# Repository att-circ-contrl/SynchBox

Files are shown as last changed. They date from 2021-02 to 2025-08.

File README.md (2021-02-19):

# "I/O SynchBox" Data Logger and Timing Signal Generator

## Overview

The I/O SynchBox is a USB-connected device designed to synchronize and
collect data from several pieces of equipment:

* It can generate two independent timing signals (TTL pulse trains on BNC).
* It can assert individual TTL pulses on two independent BNC outputs
(typically used for control of external equipment).
* It can emit 16-bit data words on a rectangular (ribbon cable) connector.
This is typically used to send "event codes" to e-phys recording equipment
and/or to eye-tracker equipment.
* It can read analog inputs on three BNC ports ("X", "Y", and "Z"; typically
analog joystick connections).
* It can read from light sensors on two BNC ports ("L" and "R"; typically
connected to an experiment computer monitor for frame synchronization).

The SynchBox has an internal real-time-clock with 0.1 ms precision. Event
reports (with timestamps) are sent to the host computer over a USB serial
link. Analog inputs are polled at a user-configured rate, and reported
(with timestamps) at the polling interval.

Clock drift is nominally 100 parts per million or better (the precision of
the clock crystal on the "Arduino Mega 2560" microcontroller board).

The I/O SynchBox project is copyright (c) 2021 by Vanderbilt University,
and is released under the Creative Commons Attribution-ShareAlike 4.0
International License.

## Quick-Start

The top-level Makefile automates common operations (under Ubuntu-derived
Linux, at least):

* Type "`make`" without arguments for the Makefile target list.

* To rebuild the manuals (which should already be in the "`manuals`" folder),
type "`make manual`".

* To flash an I/O SynchBox using the firmware hex file, plug the device
into your computer and type "`make burn`".

* To rebuild the firmware for the I/O SynchBox, make sure the "NeurAVR"
project is installed and "`neuravr`" is symlinked at an appropriate
location (in the "`code-firmware`" folder or in the folder the "`SynchBox`"
project is installed in), and type "`make hex`".

* To build release packages for all of the I/O SynchBox's hardware
components and peripherals, type "`make hwpkgs`". Board fabrication
files, meshes, and various documentation files are left in subfolders in
the "`packages`" directory.

## Remarks

This project is at a milestone state, and is in service, but future changes
are planned (eventually) that will substantially affect the project's
structure.

The present version will probably be kept as a branch, but the active version
will make major changes:

* For the time being, the firmware includes a shim that allows compiling
with the Arduino IDE instead of the NeurAVR libraries. This is not
guaranteed to be supported in the future (and might already be broken; I
haven't tested it recently).

* While the firmware does use the NeurAVR libraries, it does not presently
use the NeurAVR application skeleton. Version 2 will use that, along with
the ADC libraries and other code presently duplicated in the firmware
source. The end result will be cleaner and more compact but won't build with
the Arduino IDE (the application skeleton source would have to be transcluded
at compile-time, which may eventually be supported but not soon).

* Certain firmware features may be dropped or modified. In particular, event
code strobe  bits aren't actually used by any of our applications, and
timing pulse, reward pulse, and event code generation may be replaced with
more general GPIO signal/pattern generation code. The legacy command set will
probably be kept, for use-case compatibility, but the implementation will
change (and may be moved to a "GPIO device" application library).

* TTL input for timing synchronization really should be implemented (on BNC
lines and on the parallel header). The underlying GPIO implementation will
certainly support that when implemented.

* Right now, all of the printed circuit boards are project-specific. The
boards are very similar to those used for other ACC Lab projects, and will
eventually be merged into a single set of standard boards with as few
project-specific boards as possible. When that happens, all PCB layouts
and front-panel mechanical plans that are not SynchBox-specific will be
moved to that project.

## Folders

* `code-firmware` -- Firmware source code for the SynchBox.
* `datasheets` -- Vendor-supplied datasheets. Under vendor copyright.
* `hardware-main` -- Boards, CAM files, and drawings for the I/O SynchBox
internal components.
* `hardware-periphs` -- Boards, CAM files, meshes, and drawings for external
peripherals and accessories.
* `hexfiles` -- Firmware binaries for the SynchBox.
* `manuals` -- SynchBox documentation.
* `manuals-src` -- Source for rebuilding the SynchBox documentation.
* `notes` -- Assorted notes regarding SynchBox use and development.
* `packages` -- Automatically generated archives packaging relevant files
for making hardware components and peripherals. This typically includes a
`.zip` archive of the gerber files using the naming conventions of the
"Seeed Studio" PCB fabrication service, a `.png` rendering of the board
generated from the gerber files, a `.zip` archive containing g-code
toolpaths for various hardware parts, `.stl` files containing meshes for
various hardware parts, and other documentation as appropriate.
* `photos` -- Selected photographs of the SynchBox and its accessories.
* `utils` -- Various helper scripts.
* `vendor-docs` -- Vendor-provided documentation (other than datasheets).
Under vendor copyright.

Within each hardware component's folder the following subdirectories may be
present:

* `boards` -- Printed circuit board design files. Anything with the `.pcb`
extension was made with the "`pcb`" program (now part of `gEDA`).
* `boards/gerber` -- Files for printed circuit board fabrication as generated
by `pcb`.
* `boards/plots` -- Manually assembled renderings of the circuit board layout.
* `cad` -- CAD files (mechanical models) for cases and faceplates. Files with
the `.fcstd` extension were made with the "`FreeCAD`" program. Files with
`.iges` and `.step` extensions are models exported to industry-standard
formats that can be imported into different CAD programs.
* `diagrams` -- Illustrations that are not mechanical drawings.
* `drawings` -- Mechanical drawings of boards, cases, and faceplates.
* `mech` -- CAM files (toolpaths) for cases and faceplates. Files with the
`.crv` extension were made with Vectric's `VCut` program. Files with the
`.crv3d` extension were made with Vectric's `Aspire` program but can probably
be imported into `VCut`. Files with the `.txt` extension are g-code; the tool
for each g-code file is usually indicated in the filename.
* `meshes` -- STL meshes for 3d printed parts.
* `notes` -- Assorted design documentation not covered above.
* `packages` -- A symbolic link to the project's sub-folder in the
top-level "`packages`" directory.
* `renders` -- Renders of mechanical models of cases, faceplates, and
assemblies.
* `schematics` -- Manually generated schematics for printed circuit boards.
Anything with the `.fig` extension was made with the "`xfig`" program.

Regarding the software tools used:

* I have a love/hate relationship with the `pcb` program. It works _just_
well enough that it isn't worth my time to learn a new program, but the
parts of the interface that I use have gone steadily downhill since 2003.
It also won't check a layout against a netlist, which is vital for anything
more complicated than the boards in this project. If you need to modify
existing board layouts, I suggest importing the gerber files into your
preferred PCB CAD program rather than trying to use the design files as-is.

* I have a love/hate relationship with the `FreeCAD` program. It works
_just_ well enough that it isn't worth my time to learn a new program, but
it has very strange ideas about how many operations should be done and it
lacks several features that would be very helpful for building models. If
you need to modify existing mechanical models, I suggest importing `.step`
or `.iges` models into your preferred CAD program.

* I've had good experiences with Vectric's CAM software, and the price for
`VCut` is reasonable for hobbyists. This generates 2D toolpaths at multiple
depths, so it's fine for cases and faceplates for electronics. That said,
it should be possible to convert EPS to DXF and import DXF into any CAM
program, or to reimplement the case designs very quickly using the mechanical
drawings, so any CAM program should be sufficient if you need to generate
new toolpaths.

_This is the end of the file._

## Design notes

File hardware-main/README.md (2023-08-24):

# "I/O SynchBox" Hardware -- Main Unit

## Overview

The "I/O SynchBox" consists of a "shield" that sits on top of an "Arduino
Mega 2560" board, with ribbon-cable headers connecting the shield to
various faceplate boards. This decouples the shield design, faceplate board
design, and choice of enclosure (each may be varied without needing to
redesign the other, as long as headers are kept consistent).

**NOTE** -- Some or all of these boards will eventually be replaced with
general-purpose variants in their own project.

## Folders

* `mech-aux` --
Folder for mechanical models used by several components.
* `notes` --
Folder for auxiliary information for building the SynchBox.
* `v2-backpanel` --
Faceplate board with 8 TTL BNC connectors and a USB 2.0 B
power-and-communication port.
Fits in Hammond's aluminum box end-panels, should fit a 1u rack panel.
* `v2-frontpanel` --
Faceplate board with 5 analog input BNC ports, reset switch, status light,
and a rectangular connector with 16-bit digital output.
Fits in Hammond's aluminum box end-panels, should fit a 1u rack panel.
* `v2-shield` --
"Shield" board for use with an "Arduino Mega 2560" board. Maps analog
header pairs 4 and 5 to light sensor circuitry (pull-ups and pre-amplifier
circuits).

_This is the end of the file._

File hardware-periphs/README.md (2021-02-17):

# "I/O SynchBox" Hardware -- Peripheral Devices

## Overview

Various peripherals have been built for the "I/O SynchBox". Most of these
are used to map TTL outputs from the rectangular connector on the SyncBox
front panel to TTL inputs on other pieces of equipment. This allows "event
codes" to be sent from the SynchBox that are used to align data recorded by
the SynchBox's host computer with data recorded by these other devices.

Other peripherals exist and are noted below.

## Folders

* `adapter-brainamp` --
Adapter for a 3-row 26-pin D-sub connector used by the Brain Products
"BrainAmp" device.
* `adapter-intan` --
Adapter mapping 8-bit 10-position cables (from the "`ribbon-splitter`"
adapter) to pins that mate with the digital I/O terminal blocks on the
Intan "I/O Expander" used with Intan's "RHD" and "RHS" series recording and
stimulation controllers (respectively).
* `adapter-neuroscan` --
Adapter for a 25-pin D-sub connector used by the Compumedics "NeuroScan"
device.
* `adapter-tobii` --
Combination splitter/adapter mapping the least-significant 8 bits of the
SynchBox's TTL output to a 9-pin D-sub connector used by the Tobii "Pro
Spectrum" eye-tracker. All TTL ouputs are also passed through to a second
ribbon cable connector.
* `chuck-standalone` --
Hardware and firmware for a stand-alone device that communicates with a host
computer in a similar manner to the SynchBox, relaying data from a Nintendo
"Wii Nunchuck" joystick.
* `joystick-2016` --
Scematics for a ruggedized analog joystick used in 2016 epxierments.
* `light-sensor-clamp` --
3d printed clamp used for mounting light sensors on the corners of monitors.
Patches of the screen under the light sensor are strobed to encode data, and
the SynchBox reads the resulting analog signals to allow timing
reconstruction with sub-frame accuracy.
* `ribbon-splitter` --
Splitter converting the 16-bit 34-position rectangular connector TTL output
to two 8-bit 10-position rectangular connector outputs.

_This is the end of the file._

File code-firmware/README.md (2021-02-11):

# Attention Circuits Control Laboratory - I/O SynchBox project
# README documentation.
Written by Christopher Thomas.

## Important things to note:

* Arduino's development environment will auto-detect and include any file
that has a `.ino`, `.c`, `.cpp`, or `.h` extension.

* The Arduino IDE doesn't like hyphens in filenames; use underscores instead.

* I gave the Makefile a customized name to avoid confusing the Arduino IDE.
It will generate its own Makefile when building the project.

* **Building with the Arduino IDE is possible but not officially supported.**
There are shims in place for it, and it may be officially supported again
in the future, but for now it's not guaranteed to work.

## Building using the NeurAVR library and "`make`":

To build using the NeurAVR library, use:

`make -f Makefile.neuravr NEURAVRPATH=(path) (targets)`

Type `make` for a list of available targets. Typical targets are:

* `clean` -- Removes binaries so that the Arduino IDE doesn't complain
about them.
* `hex` -- Builds the hex files (and copies them to the top-level hex
folder).
* `burn` -- Calls `avrdude` to write the hex image to `/dev/ttyACM0`.
* `test` -- Connects to `/dev/ttyACM0` using the `cu` serial client.

The `NEURAVRPATH` variable defaults to looking for `neuravr` in the build
directory. This is a symlink to the `NeurAVR` project tree; the symlink
can be changed as an alternative to specifying a path variable.

## Building using the Arduino IDE:

* Copy (or symlink) the project directory into your Arduino sketchbook
  directory. The directory name must match the name of the top-level .ino file
  (so, "synchbox" for this project).

* Open and edit the project per normal.

* On my machine, under Linux, the Arduino IDE sometimes can't open the serial
port to burn the sketch. Once you've found the hex file, the sketch can be
burned manually using:

`avrdude -c stk500 -p m2560 -P (port) -D -U flash:w:(file):i`

...Where "`(port)`" is usually `/dev/ttyACM0` or `/dev/ttyUSB0` under Linux,
and `(file)` is the hex file.

The Arduino IDE puts the hex file in:

`/tmp/build(gibberish).tmp/(filename).hex`

Use "`ls -t /tmp|grep build|head -1`" to find the right build directory;
every build attempt will create a new directory, so there will be several
of them.

_This is the end of the file._

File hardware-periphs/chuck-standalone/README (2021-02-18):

This code is intended to interface with the "Adafruit Pro Trinket 5V", which
is a smaller-form-factor variant of the Arudino Pro/Arduino Pro Mini, using
an ATmega328P chip at 16 MHz (as with the Arduino Uno).

An Adafruit "Nunchucky" board was used as the Wii Nunchuck break-out adapter.
If memory serves, it mated directly with the digital I/O pins on the
Pro Trinket, but it's been many years so I no longer remember the details.

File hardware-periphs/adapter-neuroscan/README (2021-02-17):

This board didn't work!

I had to remove the isolator chips and bridge across their pads to make a
pass-through, instead of using isolation.

This passed multiple desk-checks against the chips' datasheets, so I'm not
sure what went wrong.

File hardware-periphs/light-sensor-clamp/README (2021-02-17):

See the LICENSE file for distribution information.

Each clamp consists of three 3D printed parts, and two McMaster-Carr parts.

The 3D printed parts are the body of the clamp (yellow in the assembly
diagram), the wire-holding cap (green in the assembly diagram), and the
sensor locator cap (red in the assembly diagram).

To assemble the clamp:

- Affix the foot (p/n 6111K451) to its feed hole in the clamp body, either
by gluing the foot's mounting nut to the body or by gluing a 1/4"-20 threaded
insert into the feed hole in the clamp body.
- Verify that the foot travels freely, and glue the knob (p/n 6214K26) to
the foot's threaded rod.
- Feed the TEPT4400 phototransistor's leads through the locator cap's holes.
- Feed the BNC pigtail's leads through the body of the clamp out of the
sensor hole.
- Solder the phototransistor's leads to the BNC pigtail's leads, using
heat shrink or tape to avoid short circuits.
- Press-fit the locator cap into the clamp body.
- Slide the wire cap on to the BNC pigtail's leads.
- Press-fit the wire cap on to the clamp body.

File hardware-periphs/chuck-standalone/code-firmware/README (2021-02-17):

Important things to note:

- Arduino's development environment will auto-detect and include any file
  that has a .ino, .c, .cpp, or .h extension.

- The Arduino IDE doesn't like hyphens in filenames; use underscores instead.

- I gave the Makefile a customized name to avoid confusing the Arduino IDE.

Using the NeurAVR library and not the Arduino IDE:

- FIXME - The NeurAVR does not yet support I2C, so building this way will
give you bogus data!

- To build using the NeurAVR library instead of using Arduino, use
"make -f Makefile.neuravr (optional target)". Default target is "hex";
"clean" removes binaries so that the Arduino IDE doesn't complain about them.

- Development targets are "burn" (using the bootloader), "isp" (using the
AVRispMk2 programmer), and "test" (trying to contact using "cu"). These only
work on my personal machines; you'll have to edit them to get them working
on your systems (these are convenience-targets; these tasks can be done
manually easily enough).

Using the Arduino IDE:

- On my machine, under Linux, the Arduino IDE sometimes can't open the serial
  port to burn the sketch. The sketch can be burned manually via:

  avrdude -c stk500 -p m2560 -P /dev/ttyACM(number) -U flash:w:(hex file):i

  (The -D flag may also be needed if flash-erase fails.)

  The Arduino IDE puts the hex file in
  /tmp/build(gibberish).tmp/(filename).hex.
  Use "ls -t /tmp|grep build|head -1" to find the right build directory.

- There may also be shenanigans connecting to the serial port. To do this
  manually, use:

  cu -l /dev/ttyACM(number) -s (baud)

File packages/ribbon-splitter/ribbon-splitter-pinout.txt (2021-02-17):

On the original 34-pin header, even pins are ground, pins 1..31 are digital
outputs (LS pin 1), and pin 33 is +5V.

On the 10-pin output headers, pin 1 is ground, pins 2..9 are digital outputs
(LS pin 2), and pin 10 is ground.

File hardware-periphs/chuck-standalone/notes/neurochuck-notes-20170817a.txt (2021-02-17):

From thomasc@cse.yorku.ca Thu Aug 17 10:47:26 2017
Date: Thu, 17 Aug 2017 10:47:26 -0400 (EDT)
From: Christopher Thomas <thomasc@cse.yorku.ca>
To: Ben Voloh <ben.voloh@gmail.com>, Marcus Watson <marcusrwatson@gmail.com>
Subject: Neurochuck firmware

   In case anyone besides me wants to flash more of these, here's the 
firmware image for the version of the "neurochuck" I have now. This should 
work on any 16 MHz ATmega328P system, including the Uno and Pro Trinket.

   (The 3.3V Pro Trinket runs at 12 MHz instead, which will throw off 
timing, including baud rate timing.)

   It supplies "power" and "ground" to Ain3 (C3) and Ain2 (C2), 
respectively. It uses the LED on Dio13 (B5/SCK) for status indication. If 
you pull down Dio8 (B0) during boot, it'll start spitting out packed data 
automatically without you having to tell it to (this is how it would work 
if I put it in the Neurarduino box).

   The command interface is very similar to the Neurarduino's. Connect at 
115200 baud, type "hlp" or "?" for help, and "idq" to query the device 
type string (so that you can tell this and the neurarduino apart).

   With timestamps enabled (default for manual mode), output looks like:

   TnnnnnnnnJxxyycLxxyyzz

   Without timestamps (default for autostart mode), output looks like:

   JxxyycLxxyyzz

   Joystick (J) and accelerometer (L) values are 8-bit hex-encoded bytes. 
Button values are one hex digit (0-3 in practice; C is bit 0 and Z is 
bit 1).

   If you want a packaged version immediately, I have a case on-hand that I 
can put it into if you don't mind rough-cut holes. Otherwise let me know 
how you want me to proceed with it.

Regards,
 				-Christopher Thomas

    [ Part 2, ""  Text/PLAIN (Name: "neurochuck-20170817.hex") ~30 KB. ]
    [ Unable to print this part. ]

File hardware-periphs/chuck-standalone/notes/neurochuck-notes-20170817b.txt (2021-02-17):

From thomasc@cse.yorku.ca Thu Aug 17 15:06:30 2017
Date: Thu, 17 Aug 2017 15:06:29 -0400 (EDT)
From: Christopher Thomas <thomasc@cse.yorku.ca>
To: Ben Voloh <ben.voloh@gmail.com>
Cc: Marcus Watson <marcusrwatson@gmail.com>
Subject: Re: new nunchuk idea

   I've attached the code, and an updated hex file (I'd forgotten that 
buttons were negative-logic in the raw data; this has been fixed).

   I gave the templates for output in a previous email. Actual test-run 
output is as follows:

(no timestamps; LTS 0):

J7b801L8461b0
J7c811L7f5db2
J7b800L8160b2
J7c810L7f60b0
J7b801L7f5ab4
J7b800L805fb2
J7b800L815db0
J7c802L825eb2
J7b802L805bb1
J7b802L815db3
J7b802L805db1
J7c812L835db6
J7b802L815cb9
J7b800L8c5cad
J7b800L9b5398
J7b800L944d93
J7b800L8c4d99

(with timestamps; LTS 1, the default):

T0002d453J7cff0L8c69af
T0002d83bJ7cff0L8d57b1
T0002dc23J7bff0L8c56a9
T0002e00bJ7cff0L8d57ab
T0002e3f3J7cff0L8d57ac
T0002e7dbJ7cff0L8d58ad
T0002ebc3J7bff0L8d58ad
T0002efabJ7cff0L8f56a8
T0002f393J7b800L984d9a
T0002f77bJ7b800La04d91
T0002fb63J7b800L866196
T0002ff4bJ7b800L628493
T00030333J7c800L1995a5
T0003071bJ7b800L37848c
T00030b03J7b800L3b8988
T00030eebJ7b800L468c91
T000312d3J7b800L468595

(the status screen; QRY):

System state (all values in base 10):
   Version:  20170810
   Timestamp:  54900 ticks
   Clock ticks per second:  10000
   Nunchuck detected:  YES
   Nunchuck polling interval:  100 ticks
   Nunchuck data scrambling:  OFF
   Automatic start:  NO
   Logging:  OFF
   Log interval:  1000 ticks
   Log timestamps:  ON
   Blink codes:  ON
   Clock ticks per blink code bit:  625
End of system state.

(the identity string; IDQ):

devicetype: Neurochuck  subtype: v1  revision: 20170810

(the help screen; HLP or ?):

Commands:
  ?, HLP  :  Help screen.
     QRY  :  Query system state.
   ECH 1/0:  Start/stop echoing typed characters back to the host.
     IDQ  :  Device identification string query.
     INI  :  Reinitialize (clock reset and events idled).
   LOG 1/0:  Start/stop reporting log data.
     LIN n:  Set the data reporting interval to n ticks.
   LTS 1/0:  Include/don't include timestamps in log reports.
     KIN n:  Set the nunchuck polling interval to n ticks.
   BLN 1/0:  Enable/disable status LED blinking.

Regards,
 				-Christopher Thomas

    [ Part 2, ""  Application/X-TAR (Name: "neurochuck-20170817.tar") 84 ]
    [ KB. ]
    [ Unable to print this part. ]

    [ Part 3, ""  Text/PLAIN (Name: "neurochuck-20170817-5v.hex") ~30 KB. ]
    [ Unable to print this part. ]

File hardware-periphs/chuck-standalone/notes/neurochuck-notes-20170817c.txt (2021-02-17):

From thomasc@cse.yorku.ca Thu Aug 17 15:11:46 2017
Date: Thu, 17 Aug 2017 15:11:46 -0400 (EDT)
From: Christopher Thomas <thomasc@cse.yorku.ca>
To: Ben Voloh <ben.voloh@gmail.com>
Cc: Marcus Watson <marcusrwatson@gmail.com>
Subject: Re: new nunchuk idea

   As with the Neurarduino code, you can dump it all into a sketchbook 
directory and build it using the IDE as-is, or you can use "make -f 
Makefile.neuravr" to build against the "neuravr" libraries that I'd made 
for the Neurarduino and related hardware.

   The custom libraries don't have I2C yet, so I recommend using the 
Arduino IDE if you want it to actually sense nunchuck data.

   To talk to the dongle, connect via USB serial port at 115200 baud.

   The status LED is blinking on and off when it can't find the nunchuck, 
is solid-on with an off-blip every 2 seconds when it found the nunchuck 
but you haven't requested data, and is off with a pair of on-blips every 2 
seconds when it's streaming data to you.

   Pulling digital pin 8 to ground triggers "automatic" mode, where it 
starts streaming on startup rather than waiting for you to ask it to. In 
that mode, it omits timestamps and sends data as fast as possible 
(equivalent to LIN 0, KIN 0, LTS 0, LOG 1).

   I'll bring the dongle (and Marcus's Neurarduino) back to Marcus's desk 
as soon as I've finished taking measurements for the case.

Regards,
 				-Christopher Thomas

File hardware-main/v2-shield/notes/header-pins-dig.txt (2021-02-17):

Pin mappings for "digital I/O" header (10-pin, back panel BNC):

Header		Function		Arduino		Atmel

D0		debug input		D6		H3
D1		debug output		D7		H4
D2					D8		H5
D3					D9		H6
D4		reward B		D10		B4
D5		reward			D11		B5
D6		sync			D12		B6
D7		sync B			D13		B7

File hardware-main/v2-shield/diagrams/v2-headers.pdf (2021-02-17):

Vdd

Gnd

## Digital I/O

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
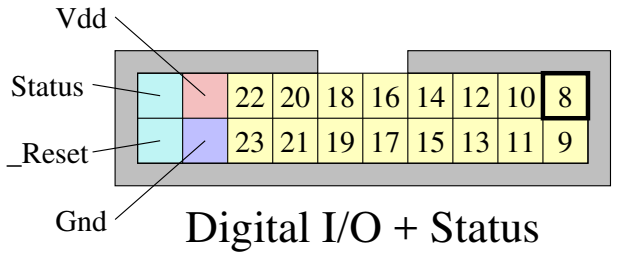
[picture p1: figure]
Digital I/O + Status; Gnd; Status; _Reset; Vdd
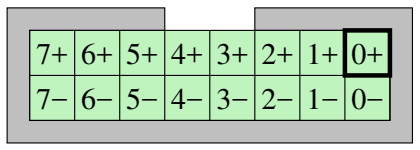
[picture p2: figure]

## Analog Input

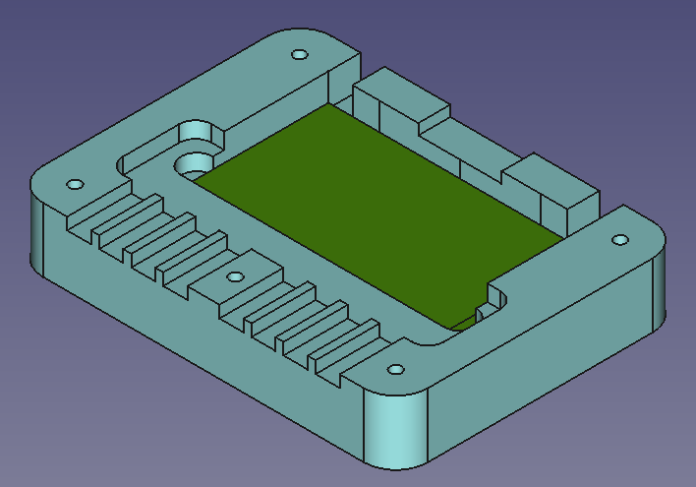
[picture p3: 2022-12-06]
hardware-periphs/ribbon-squid/renders/evcode-squid-shell-bottom.png

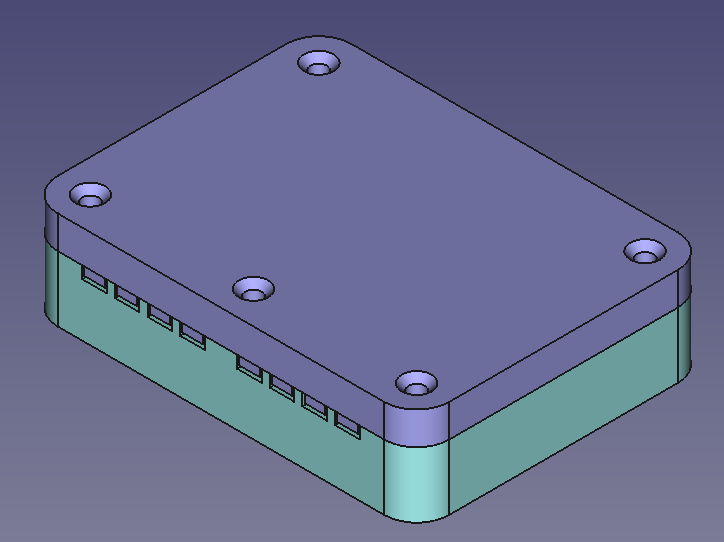
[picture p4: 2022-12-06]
hardware-periphs/ribbon-squid/renders/evcode-squid-shell-closed.png

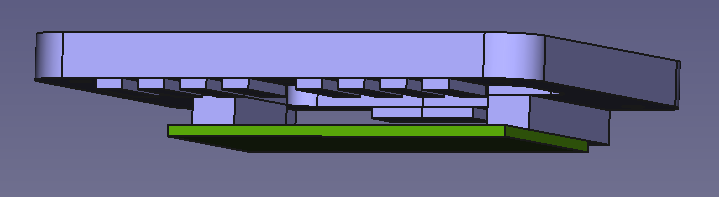
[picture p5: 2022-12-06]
hardware-periphs/ribbon-squid/renders/evcode-squid-shell-top.png

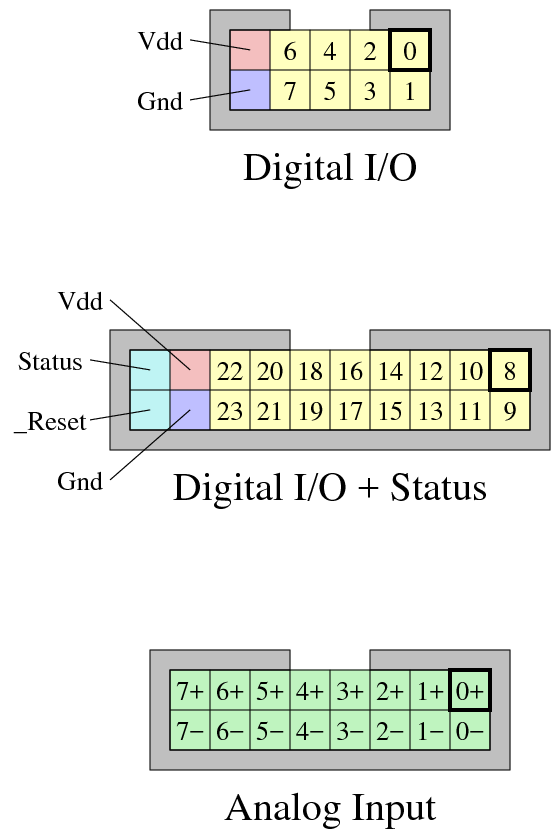
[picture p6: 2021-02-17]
hardware-main/v2-shield/diagrams/v2-headers.png

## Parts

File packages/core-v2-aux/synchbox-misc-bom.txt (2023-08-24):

Bill of materials for additional components for assembling the v2 SynchBox:

Item                             Digikey p/n          Qty

Arduino Mega 2560                1050-1018-ND           1

box metal/abs 8.7"x6.5"          HM906-ND               1

standoff nylon 4-40 F-F 3/4"     36-1902D-ND            4
screw nylon 4-40 3/4"            H550-ND                4
screw nylon 4-40 1/4"            H542-ND                4
hex nut nylon 4-40               36-9605-ND             4

USB A-B cable 6'                 1175-1089-ND           1

This is the end of the file.

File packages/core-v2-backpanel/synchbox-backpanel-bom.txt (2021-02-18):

Bill of materials for the v2 SynchBox back panel:

Item                    Digikey p/n          Qty

header male 2x5 shr     S9169-ND               1

BNC jack (pcb) 50 ohm   WM5278-ND              8

ribbon cable 10pos 6"   H3DDS-1006G-ND         1
USB B panel mount       1528-1570-ND           1

spacer nylon #4 1/16"   492-1071-ND            4
screw metal 4-40 3/8"   HM1456-ND              4
hex nut nylon 4-40      36-9605-ND             4

This is the end of the file.

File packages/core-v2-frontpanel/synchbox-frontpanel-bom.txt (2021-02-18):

Bill of materials for the v2 SynchBox front panel:

Item                    Digikey p/n          Qty

header male 2x8 shr     S9171-ND               1
header male 2x10 shr    S9172-ND               1
header male 2x17 shr    OR984-ND               1

BNC jack (pcb) 50 ohm   WM5278-ND              5
LED green 3mm           4303F5-ND              1
switch pb SPST          SW1021CT-ND            1

ribbon cable 16pos 6"   H3DDS-1606G-ND         1
ribbon cable 20pos 6"   H3DDS-2006G-ND         1

spacer nylon #4 1/16"   492-1071-ND            4
screw metal 4-40 3/8"   HM1456-ND              4
hex nut nylon 4-40      36-9605-ND             4

This is the end of the file.

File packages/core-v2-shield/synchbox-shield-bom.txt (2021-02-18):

Bill of materials for the v2 SynchBox shield:

Item                    Digikey p/n          Qty

header male 1x8         732-5321-ND            5
header male 1x10        732-2670-ND            1
header male 2x18        732-5309-ND            1
header female 2x3       S7071-ND               1
header male 2x5 shr     S9169-ND               1
header male 2x8 shr     S9171-ND               1
header male 2x10 shr    S9172-ND               1

resistor 0805 4.7 ohm   311-4.70CRCT-ND        1
resistor 0805 680 ohm   311-680CRCT-ND         1
resistor 0805 1 kohm    311-1.00KCRCT-ND       2
resistor 0805 2.2 kohm  311-2.20KCRCT-ND       2
resistor 0805 5.49 kohm 311-5.49KCRCT-ND       2
resistor 0805 6.8 kohm  311-6.80KCRCT-ND       2
resistor 0805 10 kohm   311-10.0KCRCT-ND       4
resistor 0805 47 kohm   311-47.0KCRCT-ND       3
resistor 0805 470 kohm  311-470KCRCT-ND       12
resistor 0805 10 Mohm   311-10.0MCRCT-ND       4

inductor smt 0.47mH     732-6801-1-ND          1

capacitor 1210 47 uF    399-5514-1-ND          4
capacitor 0805 10 uF    399-8012-1-ND          2
capacitor 0805 0.33 uF  399-11172-1-ND         2
capacitor 0805 0.1 uF   399-1170-1-ND          2

AD8616 op-amp 8-soic    AD8616ARZ-ND           2
AD8226 inst amp 8-soic  AD8226ARZ-ND           2

This is the end of the file.

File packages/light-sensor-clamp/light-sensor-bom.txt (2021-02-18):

Bill of materials for the SynchBox light sensor (per pair):

Item                    Digikey p/n          Qty

phototransistor         751-1057-ND            2
BNC to wire cable       314-1190-ND            2
BNC cable 6'            ACX1799-ND             2

Item                 McMaster-Carr p/n       Qty

leveling foot        6111K451                  2
threaded knob        6214K26                   2

This is the end of the file.

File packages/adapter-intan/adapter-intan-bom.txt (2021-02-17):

Small ribbon to Intan terminal block board:

Item				Digikey p/n	Unit Price	Qty	Cost

header male 2x5 shr		S9169-ND	0.42		1	0.42
header male 3.5mm 4pos		WM12840-ND	0.63		1	0.63
header male 3.5mm 3pos		WM20447-ND	0.47		2	0.94

Total									1.99

Cabling:

Item				Digikey p/n	Unit Price	Qty	Cost

cable idc 2x5 female 18"	H3DDH-1018-G-ND	1.51		2	3.02

Total									3.02

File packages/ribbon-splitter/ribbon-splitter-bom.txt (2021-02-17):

Splitter board, R/A version:

Item				Digikey p/n	Unit Price	Qty	Cost

header male ra 2x5 shr		S9177-ND	0.63		2	1.26
header male ra 2x17 shr		S9182-ND	1.20		1	1.20

Total									2.46

Splitter board, vertical version:

Item				Digikey p/n	Unit Price	Qty	Cost

header male 2x5 shr		S9169-ND	0.42		2	0.84
header male 2x17 shr		S9174-ND	0.68		1	0.68

Total									1.52

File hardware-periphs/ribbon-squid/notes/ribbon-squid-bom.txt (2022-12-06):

Board:

(1x)  prototyping board (SBB1602-1-ND)
https://www.digikey.ca/en/products/detail/chip-quik-inc/SBB1602-1/5978264

(8x)  bnc wire cable (314-1190-ND)
https://www.digikey.ca/en/products/detail/mueller-electric-co/BU-P4969/4073809

(1x) 10-position ribbon cable socket to wire (H1DXH-1036G-ND)
https://www.digikey.ca/en/products/detail/assmann-wsw-components/H1DXH-1036G/999196

Accessories:

(8x) 36" BNC cable (ACX1795-ND)
https://www.digikey.ca/en/products/detail/amphenol-rf/115101-19-36-00/2504546

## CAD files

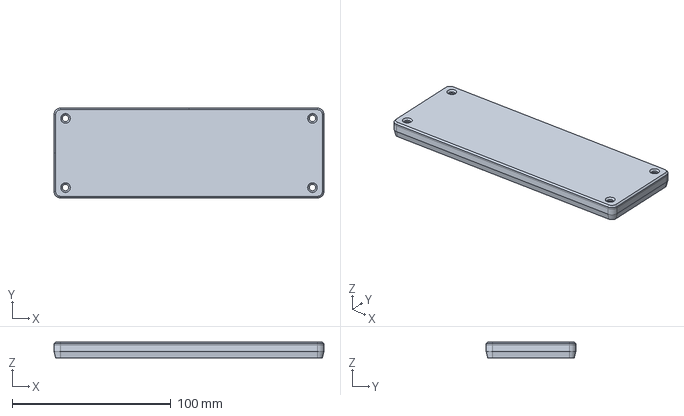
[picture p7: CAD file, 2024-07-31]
hardware-main/mech-aux/faceplate-hm904-blank-printable.iges
170.0 x 56.5 x 10.0 mm

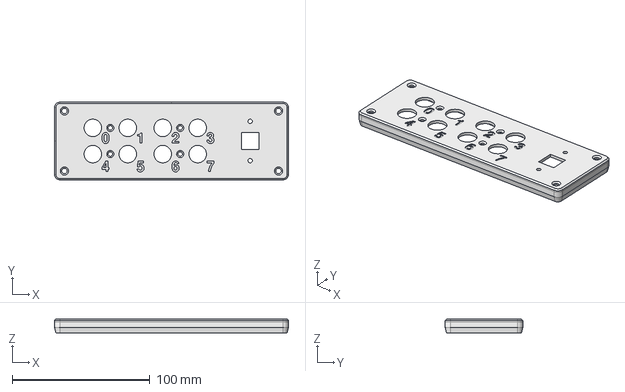
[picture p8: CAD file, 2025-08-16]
hardware-main/v2-backpanel/cad/v2-backpanel.fcstd
170.0 x 56.5 x 10.0 mm

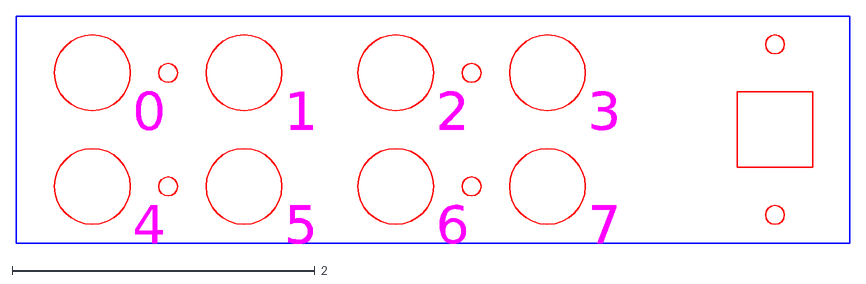
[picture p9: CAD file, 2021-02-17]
hardware-main/v2-backpanel/mech/carve-king/v2-back.dxf
0
1
2
3
4
5
6
7

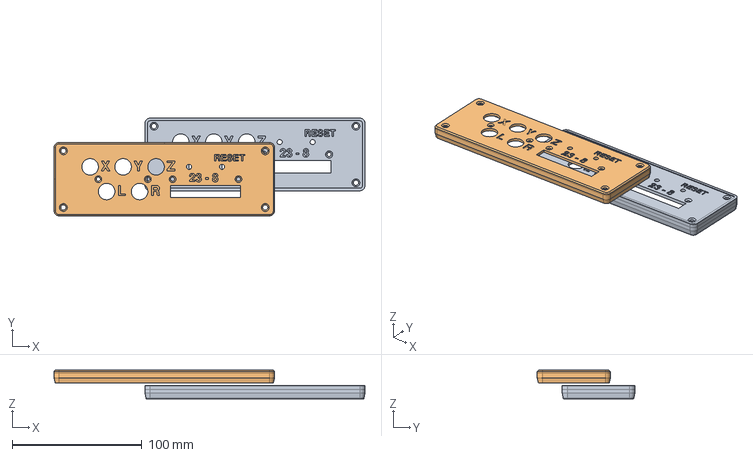
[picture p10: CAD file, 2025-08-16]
hardware-main/v2-frontpanel/cad/v2-frontpanel.fcstd
239.6 x 75.3 x 22.1 mm
front panel body
simple front panel body

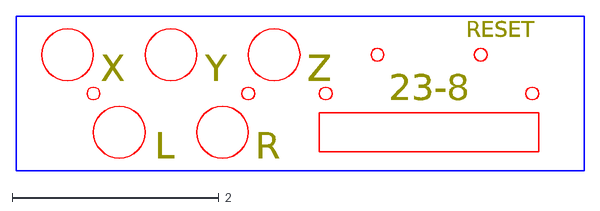
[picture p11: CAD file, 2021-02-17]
hardware-main/v2-frontpanel/mech/carve-king/v2-front.dxf
X
Y
Z
L
R
23-8
RESET

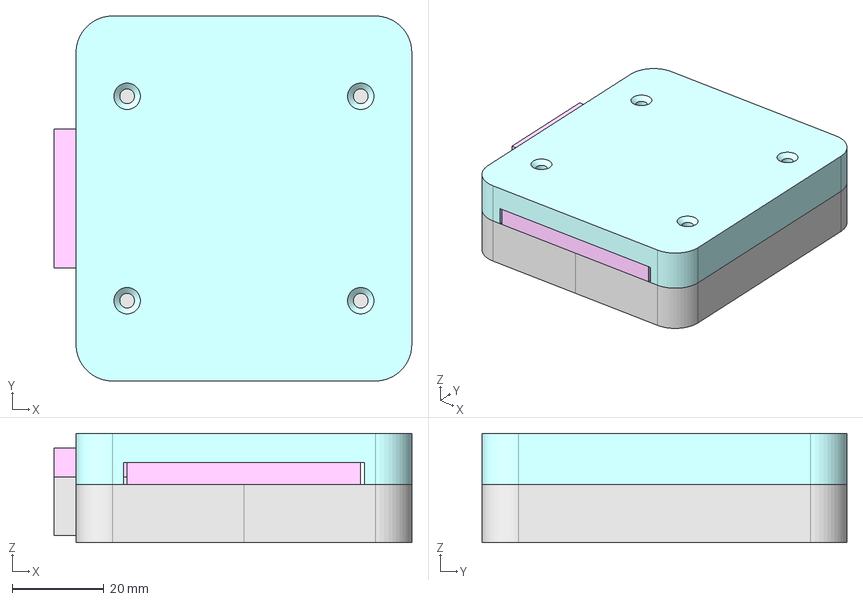
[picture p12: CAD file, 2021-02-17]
hardware-periphs/adapter-tobii/cad/tobii-adapter-shell.fcstd
77.8 x 79.4 x 23.8 mm
top shell with countersink
board slab
board with rect headers
board with db9 header
board orig
shell slab
shell with posts
shell with posts copy
shell with hollow
bottom shell with cutouts
bottom shell with holes
bottom shell with lip
top shell with rect cutouts
top shell with db9 cutout
top shell with lip
bottom shell orig
top shell orig

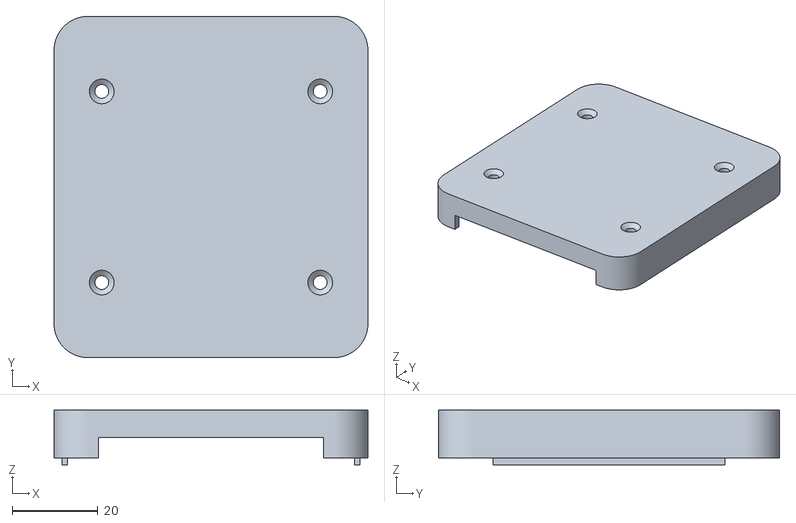
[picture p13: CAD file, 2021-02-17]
hardware-periphs/adapter-tobii/meshes/tobii-shell-top.stl
73.0 x 79.4 x 12.7

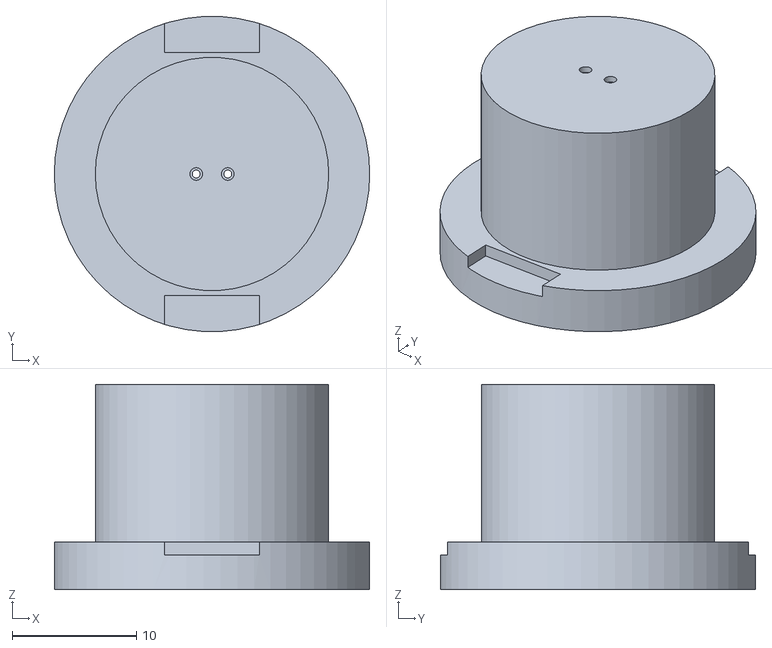
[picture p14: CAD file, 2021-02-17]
hardware-periphs/light-sensor-clamp/meshes/alternate/clamp-locator-cap-mm.stl
25.4 x 25.4 x 16.5

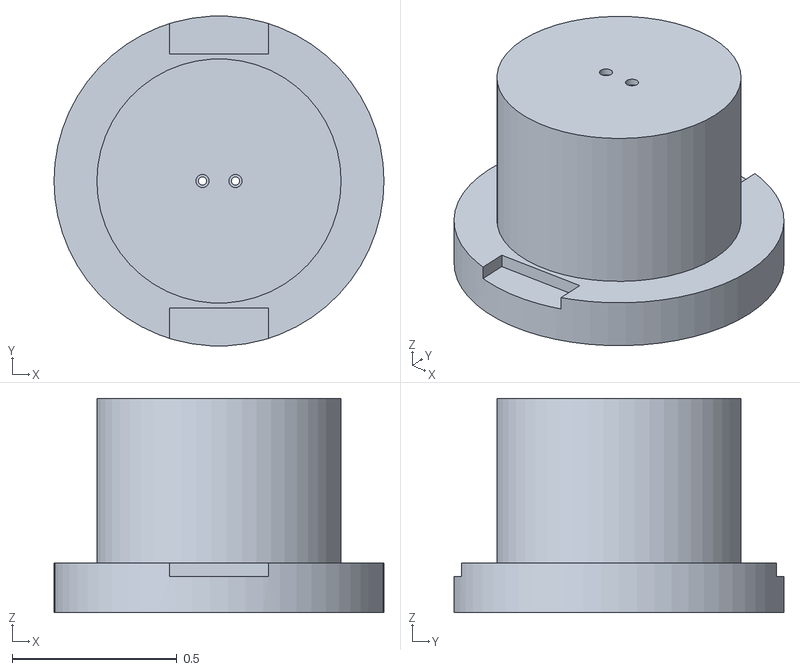
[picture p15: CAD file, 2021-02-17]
hardware-periphs/light-sensor-clamp/meshes/clamp-locator-cap-inches.stl
1.00 x 0.999 x 0.65

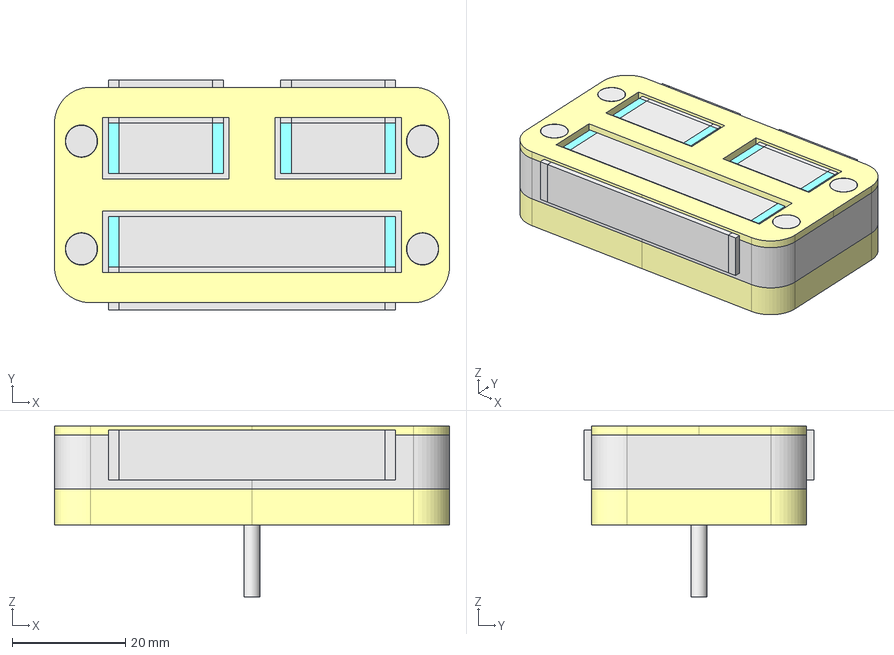
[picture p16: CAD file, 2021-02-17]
hardware-periphs/ribbon-splitter/cad/evbig-shell.fcstd
69.8 x 40.6 x 30.2 mm
shell vert top with countersink
board slab
board with vert headers
board vert orig
vert mockup board
screw head
screw with body
screw #4-40 1/4" pan
screw #4-40 3/4" pan
board slab copy
board with ra headers
board ra orig
shell slab 3/8"
shell vert bottom with posts
vert mockup board screw 1
vert mockup board screw 2
vert mockup board screw 3
shell slab with pocket
shell vert bottom with holes
shell vert bottom with lip
shell vert bottom orig
shell vert top slab
shell vert top with lip
shell vert top with cutouts
vert mockup top
shell vert top orig
vert mockup bottom
flat screw
screw #4-40 3/4" flat
screw #4-40 5/8" flat
vert mockup case screw 1
vert mockup case screw 2
vert mockup case screw 3
vert mockup case screw 4

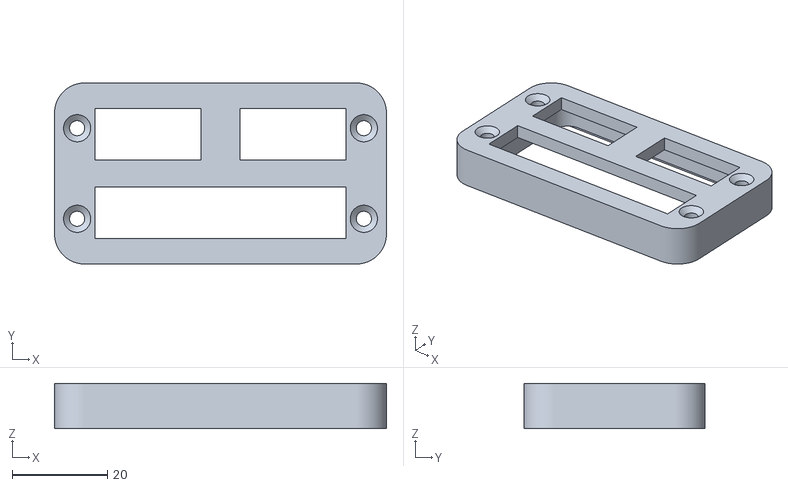
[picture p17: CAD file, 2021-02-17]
hardware-periphs/ribbon-splitter/meshes/shell-vert-top.stl
69.8 x 38.1 x 9.53

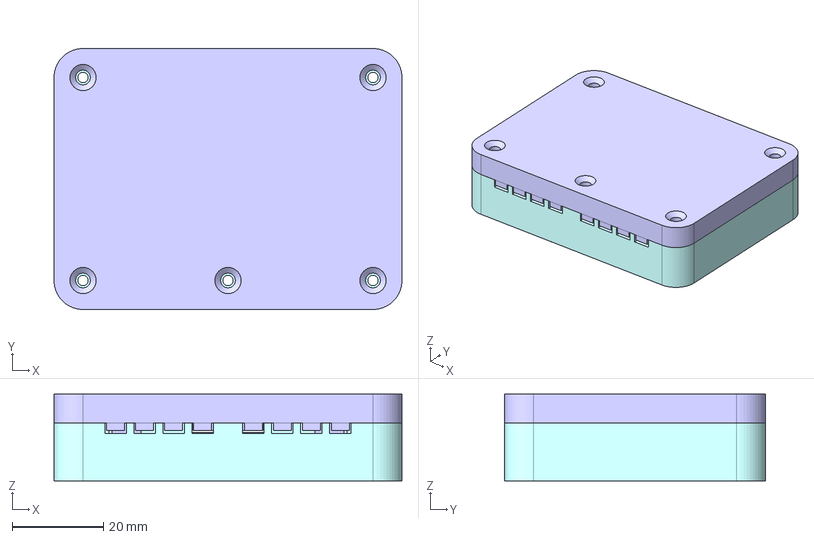
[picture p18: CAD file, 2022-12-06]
hardware-periphs/ribbon-squid/cad/event-squid-8bit.fcstd
76.2 x 57.2 x 19.0 mm
pcb copy
bottom shell copy
top shell copy

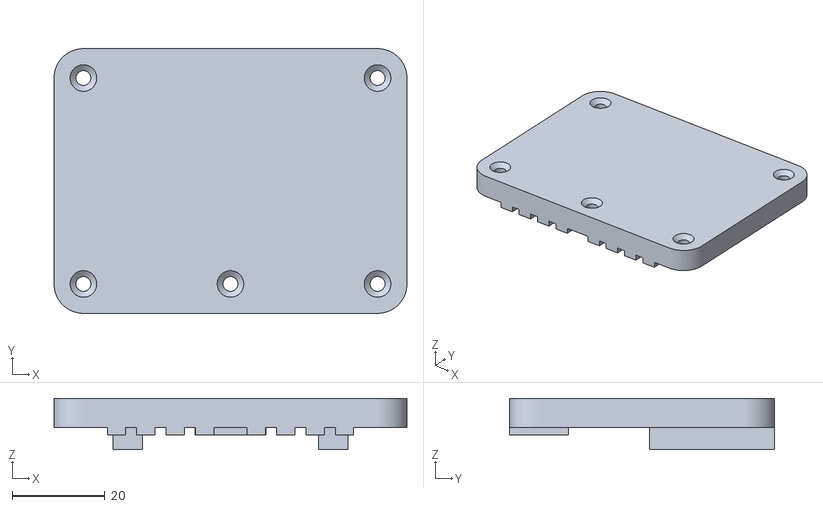
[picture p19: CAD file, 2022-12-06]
hardware-periphs/ribbon-squid/meshes/evcode-squid-top-shell.stl
76.2 x 57.1 x 11.1

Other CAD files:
hardware-main/v2-backpanel/iges/v2-backpanel-simple.iges
hardware-main/v2-backpanel/meshes/v2-backpanel-simple.stl
hardware-main/v2-frontpanel/iges/v2-frontpanel-simple.iges
hardware-main/v2-frontpanel/meshes/v2-frontpanel-simple.stl
packages/core-v2-backpanel/synchbox-backpanel-simple-model.iges
hardware-main/mech-aux/faceplate-hm904-blank.iges
hardware-main/v2-backpanel/iges/v2-backpanel.iges
hardware-main/v2-backpanel/meshes/v2-backpanel.stl
hardware-main/v2-frontpanel/iges/v2-frontpanel.iges
hardware-main/v2-frontpanel/meshes/v2-frontpanel.stl
hardware-periphs/adapter-tobii/meshes/tobii-shell-bottom.stl
hardware-periphs/light-sensor-clamp/meshes/clamp-body-inches.stl
hardware-periphs/light-sensor-clamp/meshes/clamp-wire-cap-inches.stl
hardware-periphs/ribbon-splitter/meshes/shell-vert-bottom.stl
hardware-periphs/ribbon-squid/meshes/evcode-squid-bottom-shell.stl
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

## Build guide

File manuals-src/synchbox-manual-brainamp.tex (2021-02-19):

% SyncBox manual - BrainAmp Adapter
% Written by Christopher Thomas.
%
% Copyright (c) 2021 by Vanderbilt University. This work is released under
% the Creative Commons Attribution-ShareAlike 4.0 International License.

\chapter{BrainAmp Adapter}
\label{sect-brainamp}

An adapter was constructed that allows connection of a BrainAmp unit in 
place of a NeuraLynx unit (connecting to the 26-pin ``trigger'' port). 
Data emitted over the NeuraLynx interface shows up as S-type and R-type 
markers in the BrainAmp data (with the least significant byte mapping to 
S values and the most significant byte mapping to R values).

Pin mappings are listed in Table \ref{tab-brainamp-pins}, with physical 
connector information shown in Figure \ref{fig-brainamp-pinouts}. A layout 
plot is provided in Figure \ref{fig-brainamp-pcb}.

\begin{table}[hp]
\begin{center}
\begin{tabular}{|ll|ll|}
%
\hline
\textbf{NeuraLynx pin} & \textbf{Function} & \textbf{BrainAmp pin} & 
\textbf{Function} \\
\hline
 1 & D0  & 14 & D00 (S 1) \\
 3 & D1  &  2 & D01 (S 2) \\
 5 & D2  & 15 & D02 (S 4) \\
 7 & D3  &  3 & D03 (S 8) \\
\hline
 9 & D4  & 16 & D04 (S 16) \\
11 & D5  &  4 & D05 (S 32) \\
13 & D6  & 17 & D06 (S 64) \\
15 & D7  &  5 & D07 (S 128) \\
\hline
17 & D8  & 18 & D08 (R 1) \\
19 & D9  &  6 & D09 (R 2) \\
21 & D10 & 19 & D10 (R 4) \\
23 & D11 &  7 & D11 (R 8) \\
\hline
25 & D12 & 20 & D12 (R 16) \\
27 & D13 &  8 & D13 (R 32) \\
29 & D14 & 21 & D14 (R 64) \\
-- & (ground) & 9 & D15 (R128) \\
31 & (strobe) & -- & (not connected) \\
\hline
%
\end{tabular}
\end{center}
\caption{NeuraLynx to BrainAmp pin mappings.}\label{tab-brainamp-pins}
\end{table}

\begin{figure}[hp]
\begin{center}

\end{center}
\caption{NeuraLynx and BrainAmp connector pinouts.}
\label{fig-brainamp-pinouts}
\end{figure}

\begin{figure}[p]
\begin{center}

\end{center}
\caption{BrainAmp adapter PCB layout.}\label{fig-brainamp-pcb}
\end{figure}

%
% This is the end of the file.

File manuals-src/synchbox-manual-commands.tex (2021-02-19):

% SyncBox manual - Command Interface
% Written by Christopher Thomas.
%
% Copyright (c) 2021 by Vanderbilt University. This work is released under
% the Creative Commons Attribution-ShareAlike 4.0 International License.

\chapter{Command Interface}
\label{sect-commands}

The {\projectname} is connected to the host computer via a USB serial link at 
115200 baud. The host issues commands, and the {\projectname} reports events 
that occur.

The {\projectname} issues timing pulses at regular intervals; issues reward 
pulses as one-off events; writes parallel event code data to the ephys I/O
port; and reports analog input from the joystick and light sensors at regular 
intervals.

In addition to analog light sensor values, the {\projectname} also reports
whether each sensor is above- or below-threshold. Light sensor thresholds
are calibrated by measuring sensor values during a time window, taking the 
average of these measured values, and then saving the average as the new 
threshold (overwriting the old threshold). 
``Free-running'' calibration does this repeatedly (starting a new window 
when the old window ends).

A list of available commands is shown in Figure \ref{fig-commands}. A timing
diagram of user-commanded output events is shown in Figure \ref{fig-timing}.
A diagram illustrating light sensor filtering is shown in Figure
\ref{fig-filtering}.

\begin{figure}[p]
\verbatiminput{captures/capture-help.txt}
\caption{Command summary.}\label{fig-commands}
\end{figure}

\begin{figure}[p]
\begin{center}

\end{center}
\caption{Output signal timing diagram.}\label{fig-timing}
\end{figure}

\begin{figure}[p]

\caption{Light sensor filtering.}
\label{fig-filtering}
\end{figure}

Sample output (including echoed commands) is shown in Figure 
\ref{fig-output}. Format details for verbose, terse, and packed log entries
are given in Figure \ref{fig-formats}. Typical configuration/status
information is shown in Figure \ref{fig-status}.

There are several important things to note about interactions with the 
{\projectname}:

\begin{itemize}
\item The command parser does \textbf{not} recognize backspaces.

\item \textbf{All times}, whether they're timestamps or duration 
arguments, are given in \textbf{``clock ticks'', not milliseconds}. By 
default, clock ticks are 0.1~ms in length. One second is 10000 ticks.

Milliseconds would not have been sufficiently precise, and microseconds 
would have overflowed a 32-bit counter in slightly more than one hour.

Bear in mind that the maximum argument value is 65535 (a duration or 
interval of about 6.5 seconds).

% FIXME - Force a page break.
\clearpage
\item Number values entered by the user are given in \textbf{decimal}, but 
number values reported from the {\projectname} are in \textbf{hexadecimal} 
(with the exception of status information).

Processing user information in decimal made the command parser simpler 
(and makes life easier for manually entering data). Reporting information 
in hexadecimal makes output more compact (important for high data rate 
output), and avoids time-consuming data conversion (converting to 
hexadecimal does not require divisions, only bit-shifts; converting to 
decimal does require divisions). The data rate is high enough that this 
matters.
\end{itemize}

The data reporting rate is limited by the serial connection. If events 
occur too fast to report (or if full-rate analog debug reporting exceeds the
serial connection's ability to report), reports will be dropped. Events 
themselves will still occur.

At 115200 baud, the maximum reporting rate without packet loss is 150~Hz
with verbose logging, 200~Hz with terse logging, and 300~Hz with packed
hex logging.

\begin{figure}[p]
\verbatiminput{captures/capture-messages.txt}
\caption{Sample {\projectname} output.}\label{fig-output}
\end{figure}

\begin{figure}[p]

\caption{Log entry format details.}
\label{fig-formats}
\end{figure}

\begin{figure}[p]
\verbatiminput{captures/capture-status.txt}
\caption{{\projectname} identification string and status report.}
\label{fig-status}
\end{figure}

%
% This is the end of the file.

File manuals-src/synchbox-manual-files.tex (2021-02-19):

% SyncBox manual - Project files and build environment
% Written by Christopher Thomas.
%
% Copyright (c) 2021 by Vanderbilt University. This work is released under
% the Creative Commons Attribution-ShareAlike 4.0 International License.

\chapter{Project Files}
\label{sect-files}

\fixme{This is out of date as of December 2018.}

The following folders contain the CAD files, code, and documentation for 
the {\projectname} project:

\begin{center}
\begin{tabular}{lcl}
\textbf{sketch}     & ~~ & Arduino firmware working directory. \\
\textbf{hexfiles}   & ~~ & Arduino firmware binary releases. \\
\textbf{pcb}        & ~~ & Printed circuit board CAD files. \\
\textbf{manual}     & ~~ & User guide document files. \\
\textbf{schematics} & ~~ & Schematic drawings. Needed for the manual. \\
\textbf{datasheets} & ~~ & Datasheets for selected components. \\
\textbf{drawings}   & ~~ & Mechanical drawings. \\
\textbf{capture}    & ~~ & {\projectname} communications logs. \\
\end{tabular}
\end{center}

Relevant commentary is as follows:

\begin{itemize}
\item The ``sketch'' directory should be extracted (or symlinked) to a 
``neurarduino'' project directory within Arduino's ``sketchbook''. See the 
``README'' file in that directory for more commentary.

\item Alternatively, the ``sketch'' directory may be built using the
``neuravr'' library instead of using the Arduino development environment.
To do this, use ``make -f Makefile.neuravr''. See the ``README'' file in
the ``sketch'' directory for more commentary.

\item The ``pcb'' directory contains two subdirectories (``plots'' and 
``gerber''). The root directory contains the CAD file (edited with the 
``pcb'' CAD program from the gEDA project). The ``plots'' directory 
contains an automatically-generated postscript file and manually-generated 
XCF and PNG files. The ``gerber'' directory contains 
automatically-generated GBR files, and a script 
(``\texttt{pcb2seeed.sh}'') that converts these into a form SeeedStudio 
will accept (the ZIP archive in that directory).

\item The ``manual'' directory contains LaTeX source files for the user 
manual. Some resource files are symbolic links to files that are elsewhere 
in the project.

\item The ``schematics'' and ``datasheets'' directories contain 
human-readable information pertaining to the design of the {\projectname} 
system. Anyone redesigning the {\projectname} will likely want to read these.

\item The ``drawings'' directory contains mechanical drawings of the 
faceplate for the {\projectname} enclosure. The ``laser'' file is separated 
into layers in such a way as to facilitate importing into laser-cutter 
software.

\item The ``capture'' directory contains a sample conversation with the 
{\projectname}. Manually-extracted excerpts are used in the user manual. This 
file contains most types of traffic that will be seen when talking to the 
{\projectname}. It should be noted that echo was turned on during this 
conversation, which (prior to 2017) sometimes results in command characters
being interleaved with event data.
\end{itemize}

%
% This is the end of the file.

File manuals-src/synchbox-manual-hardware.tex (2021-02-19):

% SyncBox manual - Hardware
% Written by Christopher Thomas.
%
% Copyright (c) 2021 by Vanderbilt University. This work is released under
% the Creative Commons Attribution-ShareAlike 4.0 International License.

\chapter{Hardware}
\label{sect-hardware}

The {\projectname} was implemented as a ``shield'' that mates with a 
commercial Arduino Mega2560 r3 board. A schematic for this shield is shown 
in Figure \ref{fig-schematic}, and a layout plot in Figure \ref{fig-pcb}. 
As of January 2017, a pre-amplifier was added for the light sensor inputs;
this is indicated in simplified form in Figure \ref{fig-schematic}.

Salient features are as follows:

\begin{itemize}
\item Individual digital output signals (timing and reward) are wired to 
dedicated BNC connectors (with an additional SMB connector for the timing 
signal).

\item Joystick inputs are accepted from BNC connectors, and divided using 
pairs of 470~k$\Omega$ resistors. This maps the joystick signal range 
(0-5V) to the analog to digital converter range (0-2.56V).

\item Light sensor inputs are accepted from BNC connectors, with the 
negative terminal fed through a 10~k$\Omega$ resistor to ground. The light 
sensors are phototransistors, which behave as current sources; a 
10~k$\Omega$ resistor converts the photocurrent to a voltage large enough 
to measure reliably but small enough to leave ample headroom for device 
and light source variation.

The pre-amplifier has a gain of 10x, and performs high-pass filtering with
a time constant of several seconds to cancel DC bias. The system should be
allowed to stabilize for one minute after being connected and powered,
prior to use.

\item The NeuraLynx handshaking signals are implemented using two 
dedicated ATmega output ports, for speed of manipulation by firmware. 
The ports chosen each map to contiguous blocks of 8 pins on the Arduino 
Mega header, which are wired to an appropriate 34-pin connector.

In 16-bit mode, bit 15 is the strobe bit, and bits 0-14 are data.

In 8-bit mode, bit 15 is still the strobe bit, bits 8-14 are data, and 
bits 0-7 are always zero. \textbf{NOTE:} The user sees this as an 8-bit 
interface. The argument to ``NEU'' is 0-127.

\item A status LED is provided, to communicate diagnostic information. 
This is not presently used (it's turned on when the {\projectname} boots 
and is left on).

\item A reset switch is provided, for manual reset without power cycling. 
In practice, power cycling is likely the most convenient reset method.

\item All traces and cables are assumed to be ``electrically short'' -- 
that is, to have propagation delays very much smaller than the timescales 
relevant to the equipment being connected. This allows cable termination 
and driving impedence to be ignored.

A rule of thumb is that reflections propagate at a minimum of half the 
speed of light, and that ten round-trips is sufficient to stabilize signal 
levels. With a characteristic timescale of 0.1~ms, maximum cable length is 
about 750~m.

If connected equipment uses a sufficiently fast communications sampling
rate (50 MHz or more), reflections may become significant.
\end{itemize}

A reverse-engineered schematic of the joystick is shown in Figure 
\ref{fig-joystick}.

\begin{figure}[p]
\begin{center}

\end{center}
\caption{{\projectname} schematic.}\label{fig-schematic}
\end{figure}

\begin{figure}[p]
\begin{center}

\end{center}
\caption{Joystick schematic.}\label{fig-joystick}
\end{figure}

\begin{figure}[p]
\begin{center}

\end{center}
\caption{{\projectname} PCB layout.}\label{fig-pcb}
\end{figure}

%
% This is the end of the file.

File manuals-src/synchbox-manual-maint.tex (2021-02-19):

% SyncBox manual - Maintenance
% Written by Christopher Thomas.
%
% Copyright (c) 2021 by Vanderbilt University. This work is released under
% the Creative Commons Attribution-ShareAlike 4.0 International License.

\chapter{Maintenance}
\label{sect-maint}

From time to time, new versions of the {\projectname} firmware are released.
These can be flashed using the ``\texttt{avrdude}'' utility, which is
bundled with the Arduino development environment or may be downloaded
on its own.

To use ``\texttt{avrdude}'', plug in the {\projectname}, determine what the
name of the Arduino's USB serial device is, bring up a ``command terminal''
window, navigate to the directory with the firmware file, and type:

\texttt{avrdude -c stk500 -p m2560 -P {\bfseries (device)}
-D -U flash:w:{\bfseries (firmware file)}}

For a firmware file named ``\texttt{usesyncbox-latest.hex}'', and a
USB serial device called ``\texttt{/dev/ttyACM0}'', the result will be similar
to the following:

\begin{center}
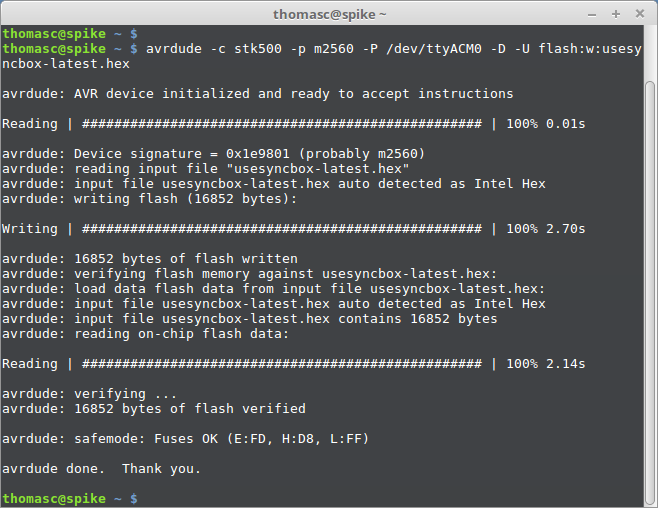
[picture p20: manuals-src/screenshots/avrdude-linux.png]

\end{center}

The names of USB serial devices vary widely from operating system to 
operating system and version to version. Consult appropriate documentation 
to determine how to find the {\projectname}'s USB serial device on your
operating system.

\section{Using \texttt{avrdude} On Linux, Windows, and MacOS}

While \texttt{avrdude} can be installed as a stand-alone package, an easy and
reliable way to install it is to install the ``Arduino'' IDE (found at:
\verb|https://www.arduino.cc|). This will install several things:
\begin{itemize}
\item The Arduino development environment.
\item The \texttt{avr-gcc} compiler and its libraries.
\item The \texttt{avr-binutils} toolchain used with \texttt{avr-gcc}.
\item The \texttt{avrdude} program for flashing AVR-based boards.
\end{itemize}

Various quirks show up on each operating system:
\begin{itemize}

\item Under Linux, you may have to add a ``udev rules'' file in /etc/udev/ to
get Arduino boards detecting and connecting properly. The Arduino IDE package
\textit{should} set this up for you.

\item Under Windows 10, neither \texttt{avrdude} nor its configuration file
will be on path by default. To use it, first find out where it was installed,
and then either type the full path name ahead of the command or add the
relevant directory to the path.
\begin{itemize}
\item To find out where \texttt{avrdude} was installed, look for an
``Arduino'' shortcut on the desktop. Right-click it to edit its properties;
this will tell you what directory the Arduino binary is in. Open the
top-level directory in that tree, and tell Windows to search that folder
to find ``avrdude''. This will bring up the directory with \texttt{avrdude}
in it, which should also contain the ``\texttt{avrdude.conf}'' configuraton
file.
\item To set the path in Windows 10, go to ``control panel'', ``system'',
``advanced system settings'', ``advanced'' tab, ``environment variables''.
Under ``user variables'', select ``path'' and click ``edit''. Add the
directory as a new entry in the list.
\end{itemize}
\item To run \texttt{avrdude} from the command line under Windows, type the
following (as one line):

\texttt{(avrdude path)/avrdude -C (avrdude path)/avrdude.conf
-c stk500 -p m2560 -P (serial port)
-D -U flash:w:(firmware file including its path)}

\item Under MacOS, \fixme{Information goes here.}

\end{itemize}

%
% This is the end of the file.

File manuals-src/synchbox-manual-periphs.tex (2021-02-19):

% SyncBox manual - Peripherals
% Written by Christopher Thomas.
%
% Copyright (c) 2021 by Vanderbilt University. This work is released under
% the Creative Commons Attribution-ShareAlike 4.0 International License.

\chapter{Accessories}
\label{sect-periphs}

Accessories produced for the {\projectname} include the following:

% FIXME - Ye web says to do one of the following for images:
% \raisebox{-\height+\baselineskip}{...}  (this fails)
% \vtop{\null\hbox{...}}  (this works)
%
\begin{tabular}{p{0.3\textwidth}p{0.65\textwidth}}
%
\vtop{\null\hbox{\
\
}} &
\vspace{\baselineskip}
\textbf{Light sensor clamps} may be attached to a wide variety of monitors
(including notebook computers). Patches of the display are strobed, and this
flickering is recorded in order to measure when frame redraws occur. \\
%
\end{tabular}

\iffalse
%
\fixme{To be photographed and added:}
\begin{itemize}
\item Old folded-thermoplastic light sensor clamps.
\item BrainAmp adapter.
\item NeuroScan adapter.
\end{itemize}
%
\fi

%
% This is the end of the file.

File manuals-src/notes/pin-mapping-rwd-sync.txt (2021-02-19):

My best guess in response to Thilo's question was:

-   Rwd:  GPIO 5 / arduino D11 / atmel B5
- Synch:  GPIO 6 / arduino D12 / atmel B6

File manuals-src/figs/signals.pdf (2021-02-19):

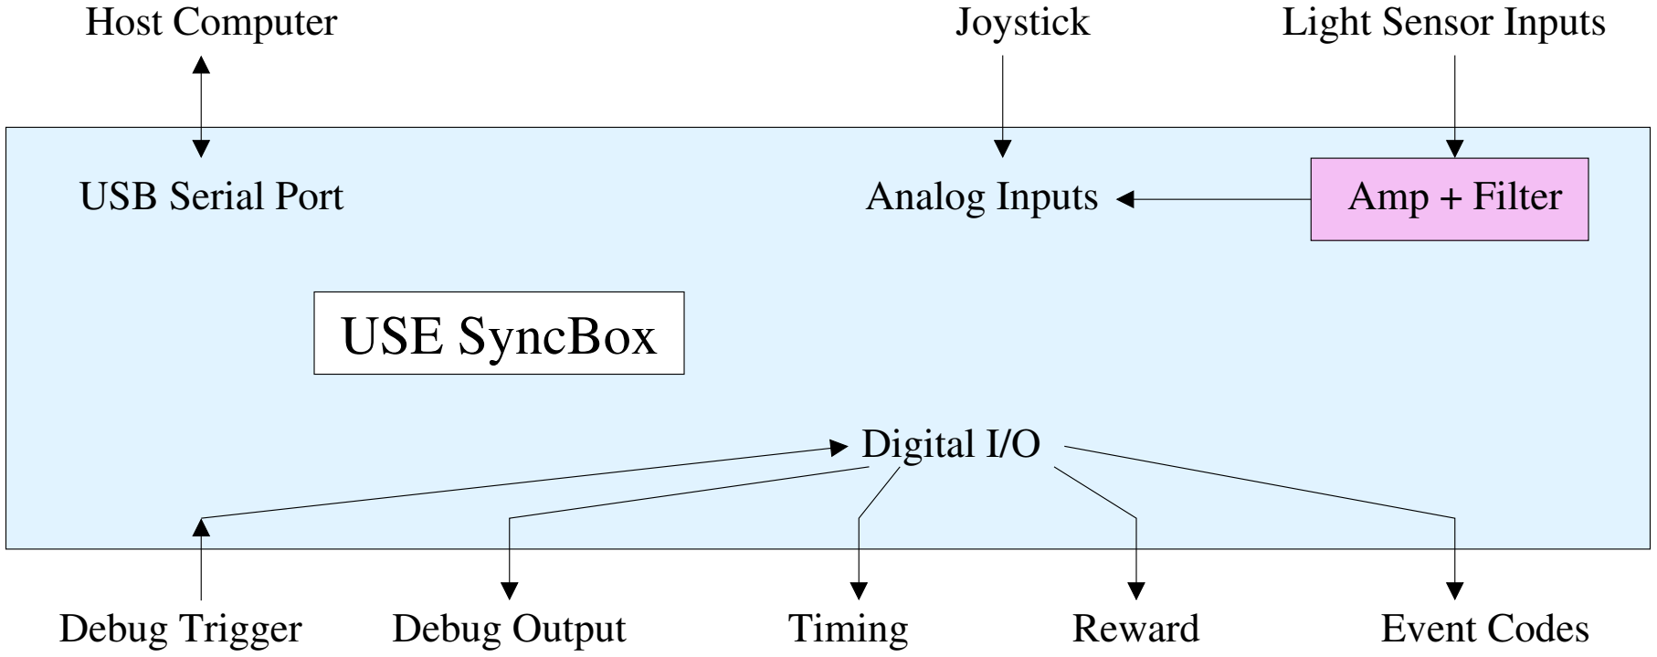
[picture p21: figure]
USE SyncBox; Host Computer; USB Serial Port; Digital I/O; Debug Trigger; Debug Output; Timing; Amp + Filter; Joystick; Analog Inputs; Light Sensor Inputs; Reward; Event Codes

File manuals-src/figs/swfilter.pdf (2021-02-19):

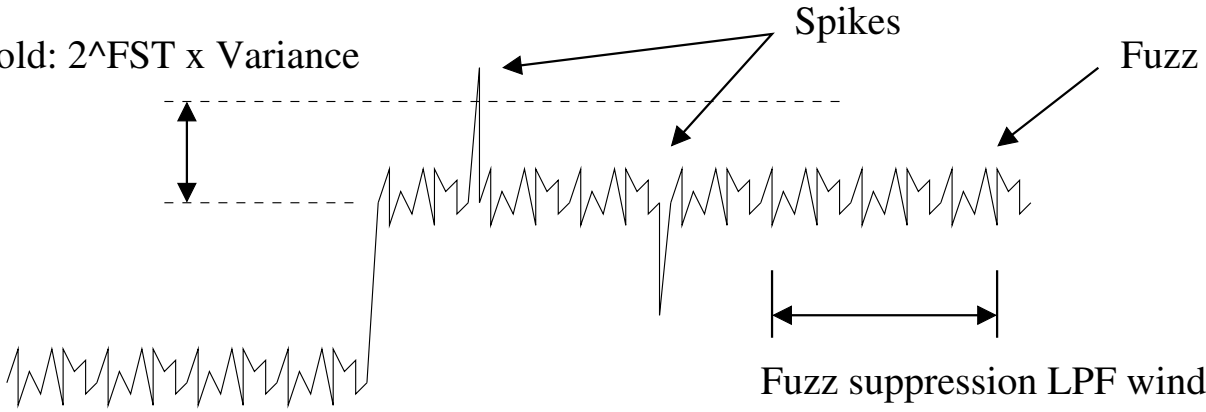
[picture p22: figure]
Spikes; Fuzz

Signal variance calculation window: 2^FSW samples

Spike rejection threshold: 2^FST x Variance

Analog sampling rate: 1 kHz

Fuzz suppression LPF window: 2^FIL samples

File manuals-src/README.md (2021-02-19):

# "I/O SynchBox" Data Logger and Timing Signal Generator - Manuals

## Quick-Start

The Makefile automates most operations involved in building the manuals.

* Type "`make clean`" to remove the manual PDFs.
* Type "`make all`" to rebuild the manual PDFs.
* Type "`make aux`" to rebuild symlinks to schematics, pinouts, etc.

The "guide" contains information needed for _using_ the SynchBox, and the
"manual" contains information needed for _developing_ the SynchBox (in
addition to a copy of the "guide" material).

## Notes

* **The manuals are very out of date.** They were last updated in 2018,
and were incomplete even then.

* The `rebuild-auxlinks.sh` script rebuilds "automated" symbolic links.
It's called by "`make aux`"; there's no need to call it directly.

## Folders

* `captures` -- Manually-edited capture text from SynchBox sessions.
* `figs` -- Diagrams drawn specifically for the manuals.
* `layouts` -- Symbolic links to layout plots from `packages` folders.
Automatically generated.
* `notes` -- Miscellaneous notes useful for writing the manuals.
* `photos` -- Symbolic links to selected images in `photos-dir`.
* `photos-dir` -- Symbolic links to the `photos` folder in the main tree.
* `pinouts` -- Symbolic links to pinout diagrams from `packages` folders.
Automatically generated.
* `schematics` -- Symbolic links to schematics from `packages` folders.
automatically generated.
* `screenshots` -- Manually-edited screenshots from SynchBox communication
sessions, firmware updating, etc.

_This is the end of the file._

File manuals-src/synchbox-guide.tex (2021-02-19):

% SynchBox manual - User Guide Top level
% Written by Christopher Thomas.
%
% Copyright (c) 2021 by Vanderbilt University. This work is released under
% the Creative Commons Attribution-ShareAlike 4.0 International License.

% FIXME - Wrap the developer manual, with switches.
%\newif\ifuserguide
%\userguidetrue
\def\userguidemarker{true}

\input{synchbox-manual}

%
% This is the end of the file.

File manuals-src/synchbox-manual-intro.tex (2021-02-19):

% SyncBox manual - Overview
% Written by Christopher Thomas.
%
% Copyright (c) 2021 by Vanderbilt University. This work is released under
% the Creative Commons Attribution-ShareAlike 4.0 International License.

\chapter{Overview}
\label{sect-over}

The {\projectname} is a device that lets a host computer and several 
instruments talk to each other. It was commissioned by the Attention 
Circuits Control Laboratory to facilitate their experiments%
\footnote{{\projectname} integration is described in:
``USE: An integrative suite for temporally-precise psychophysical
experiments in virtual environments'', Watson, M. R., Voloh, B.,
Thomas, C. J., Hasan, A. M., and Womelsdorf, T. (2018), \textit{bioRxiv},
434944  doi:10.1101/434944}.
%
A system diagram of the York University installation is shown in 
Figure \ref{fig-over-system}. A diagram of the I/O signals used by the 
{\projectname} is shown in Figure \ref{fig-over-signals}.

\begin{figure}[h]
\begin{center}

\end{center}
\caption{System block diagram.}\label{fig-over-system}
\end{figure}

% Using the float package's "yes, _really_ here" option.
\begin{figure}[H]
\begin{center}

\end{center}
\caption{{\projectname} inputs and outputs.}\label{fig-over-signals}
\end{figure}

\clearpage
The {\projectname} handles several types of communication:

\begin{itemize}

\item It talks to the host computer over a USB serial port connection.

\item It generates timing pulses. These are controlled using the 
\textbf{Txx} series of commands. These are typically used to provide
events with known timestamps to equipment such as eye-trackers and
electrophysiology instruments.

\item It generates single pulses of variable duration. These are controlled 
using the \textbf{RWD} command. These are typically used for dispensing
a reward to test animals.

\item It emits binary number values over a parallel digital interface. 
These are controlled using the \textbf{Nxx} series of commands. These are
typically used as event codes for electrophysiology equipment.

\item It reads analog information from three general-purpose analog inputs,
and shows this data during logging. These are typically used for joystick
inputs.

\item It reads light sensors to synchronize with the game computer's 
display.  The light sensor inputs have hardware amplification and filtering
(they are special-purpose inputs, not general analog inputs).
Light levels are shown during logging.

\item Logged data is controlled using the \textbf{Lxx} series of commands.

\end{itemize}

The commands are described in detail in Section \ref{sect-commands}.

To started, connect to the {\projectname} (USB serial link at 115200 baud,
8N1), and type ``\textbf{?}'' (and enter) for help. Type ``\textbf{QRY}''
to see the {\projectname}'s settings.

The front and back panels of the {\projectname} are shown in Figure
\ref{fig-panels}. The pinout of the parallel output is shown in Figure
\ref{fig-code-pinout}.

\begin{figure}[H]
\begin{center}
\begin{tabular}{lcr}

& ~~ &
 \\
\end{tabular}
\end{center}
\caption{{\projectname} front and back panels.}\label{fig-panels}
\end{figure}

\begin{figure}[H]
\begin{center}
\includegraphics[width=0.9\columnwidth]
{pinouts/synchbox-frontpanel-pinout.png}
\end{center}
\caption{Event code connector pinout.}\label{fig-code-pinout}
\end{figure}

%
% This is the end of the file.

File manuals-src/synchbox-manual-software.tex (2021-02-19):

% SyncBox manual - Firmware
% Written by Christopher Thomas.
%
% Copyright (c) 2021 by Vanderbilt University. This work is released under
% the Creative Commons Attribution-ShareAlike 4.0 International License.

\chapter{Firmware}
\label{sect-software}

The {\projectname} firmware consists of two polling loops that communicate 
via global variables. These are illustrated in Figure \ref{fig-firmware}.

\begin{figure}[h]
\begin{center}

\end{center}
\caption{{\projectname} firmware block diagram.}\label{fig-firmware}
\end{figure}

The interrupt-driven loop is called at every measurement tick (0.1~ms 
intervals), and always occurs. During each loop, it sets output pin values 
as dictated by the event queue, and it attempts to read one analog input.

The host communication loop is called via the Arduino \texttt{loop()} 
function, and repeats as frequently as it can but with no time guarantees. 
During each loop, it polls the host serial link for inbound commands, 
queues events or alters internal state based on those commands, and 
reports events that have already occurred.

State information, including the event queue and records of events that 
have recently occurred, is stored in global variables. As these may be 
updated via interrupt service routines, they are flagged as 
\texttt{volatile} and are accessed from within \texttt{ATOMIC\_BLOCK()} 
constructs when read or modified by the host communication loop 
(interrupts are already atomic).

The following aspects of the firmware should be kept in mind:

\begin{itemize}
\item Analog reads take slightly longer than 0.1 millisecond. The 
interrupt-driven loop initiates conversions only when the analog to 
digital converter is not busy. With the default configuration, this means 
one conversion every 0.2 millisecond, or one full read of all analog 
inputs every 1.0 millisecond.

Analog inputs are read sequentially (round-robin order).

\item It is possible to set the reporting rate high enough that the serial 
link cannot keep up with the requested rate. What occurs in this scenario 
is that the host communication loop reports the \textit{most recent} set 
of events that occurred every time it is polled.

The result from the user's viewpoint is that records are silently dropped. 
This situation can be detected by paying close attention to the timestamps 
of reported events (these timestamps are always accurate).
\end{itemize}

%
% This is the end of the file.

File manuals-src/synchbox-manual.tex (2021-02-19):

% SynchBox manual - Top level
% Written by Christopher Thomas.
%
% Copyright (c) 2021 by Vanderbilt University. This work is released under
% the Creative Commons Attribution-ShareAlike 4.0 International License.

\documentclass[letterpaper,11pt]{report}
\usepackage[letterpaper]{geometry}
\usepackage{graphicx}
\usepackage{verbatim}
\usepackage{float} % Needed for capital H option.

\geometry{nohead,footskip=0.3in,margin=0.75in}

% Force my paragraph style, darnit.
\usepackage{indentfirst}
\setlength{\parskip}{\baselineskip}

% Custom macros.
\newcommand{\fixme}[1]{\textbf{FIXME: #1}}
\newcommand{\projectname}{I/O SynchBox }% Remember that this eats a space.

% FIXME - Messy but better than duplicating code.
\newif\ifuserguide
\ifcsname userguidemarker\endcsname
% "User guide" switch is defined. Make sure it's set true.
\userguidetrue
\else
% "User guide" switch is not defined. Define it and set false.
\userguidefalse
\fi

%
% Document body.
\begin{document}

% Title page.

\pagestyle{empty}

\begin{center}
%
\vspace*{1in}
\ifuserguide
{\Huge \bfseries \projectname User Guide} \\
\else
{\Huge \bfseries \projectname Developer Manual} \\
\fi
{\footnotesize Written by Christopher Thomas -- \today.} \\
%
\vspace*{1.5in}

%
\vfill
{\scriptsize
Copyright (c) {\the\year} by Vanderbilt University. This work is released under
the Creative Commons Attribution-ShareAlike 4.0 International License.}
%
\end{center}
%
\clearpage
%
\pagestyle{plain}
\pagenumbering{roman}
\setcounter{page}{1}
%
\tableofcontents
%
\clearpage
\pagestyle{plain}
\setcounter{page}{1}
\pagenumbering{arabic}
% NOTE - "\thispagestyle" is used for part and chapter beginning pages,
% and overrides \pagestyle. Redefine it to be harmless.
\renewcommand{\thispagestyle}[1]{}

% FIXME - Don't break this into parts. Instead have appendices.

\input{synchbox-manual-intro}
\clearpage
\input{synchbox-manual-commands}
\clearpage
\input{synchbox-manual-periphs}
\clearpage
\input{synchbox-manual-maint}
%
\ifuserguide
% Omit developer sections for the user guide.
\else
% Include developer sections for the developer manual.
\clearpage
\input{synchbox-manual-hardware}
\clearpage
\input{synchbox-manual-software}
\clearpage
\input{synchbox-manual-files}
\clearpage

% FIXME - Accessories go here.
\appendix
\input{synchbox-manual-brainamp}
\fi

\end{document}

%
% This is the end of the file.

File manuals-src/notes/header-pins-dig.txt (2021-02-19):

../../hardware-main/v2-shield/notes/header-pins-dig.txt

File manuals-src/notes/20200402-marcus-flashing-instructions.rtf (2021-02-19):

Instructions for flashing SyncBox on Mac:

1) Install Xcode if you don’t already have it (this should be included by default with modern Macs).

2) Install homebrew if you don’t already have it, using
ruby -e "$(curl -fsSL https://raw.githubusercontent.com/Homebrew/install/master/install)" < /dev/null 2> /dev/null

3) Install avrdude if you don’t already have it, using
brew install avrdude

4) Flash the actual firmware using
avrdude -c stk500 -p m2560 -D -P PathOfSyncBox -U flash:w:PathOfHexFile:i

PathOfSyncBox and PathOfHexFile should have no quotation marks or other markers, spaces in the path may create havoc.

Some USB adapters will work when running the SyncBox normally, but not for flashing it. This has been confirmed to be the case with at least one third-party USB to USB-C adapter (error messages will include something about “timeout”. The standard Mac-made adapter worked fine.

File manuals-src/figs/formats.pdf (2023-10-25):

Time: | 0003f6ef | Joy (x/y/c): | 062a | 063f | 0647 | Opt (l/r): | 0610 | 061b | BLK | BLK
T: | 0004d853 | XYC: | 055f | 058f | 05b3 | LR: | 05b0 | 056c | B | B
T | 00054937 | J | 05b8 | 05c2 | 05c5 | L | 056f | 05cb | BB
T | 00054937 | J | 55 | 58 | 5b | L | 56 | 5c | BB

Verbose:

Terse:

Packed 16−bit:

Packed 8−bit:

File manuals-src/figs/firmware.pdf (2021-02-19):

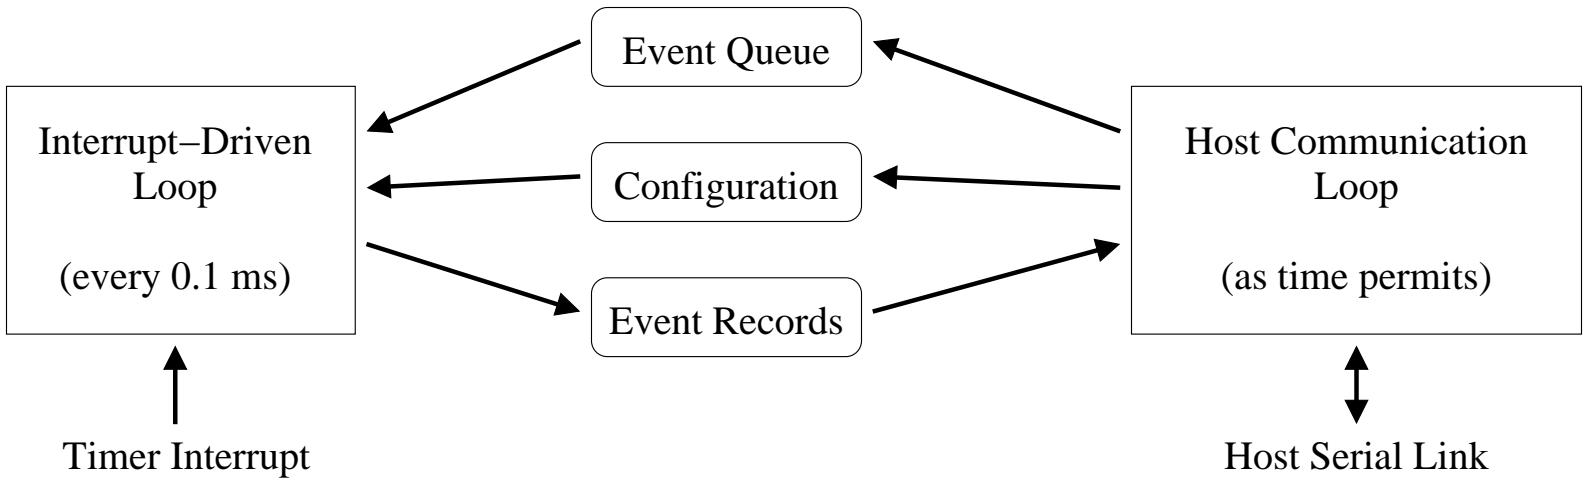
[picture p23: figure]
Interrupt−Driven Loop; (every 0.1 ms); (as time permits); Host Communication Loop; Event Queue; Configuration; Event Records; Timer Interrupt; Host Serial Link

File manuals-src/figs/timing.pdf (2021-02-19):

TPP | TPW
Timing | Reward

RWD

## Event Code

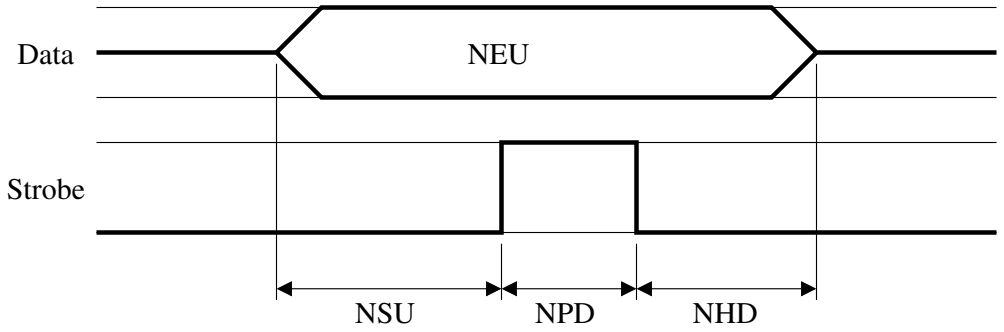
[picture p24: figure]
Data; Strobe; NSU; NPD; NHD; NEU

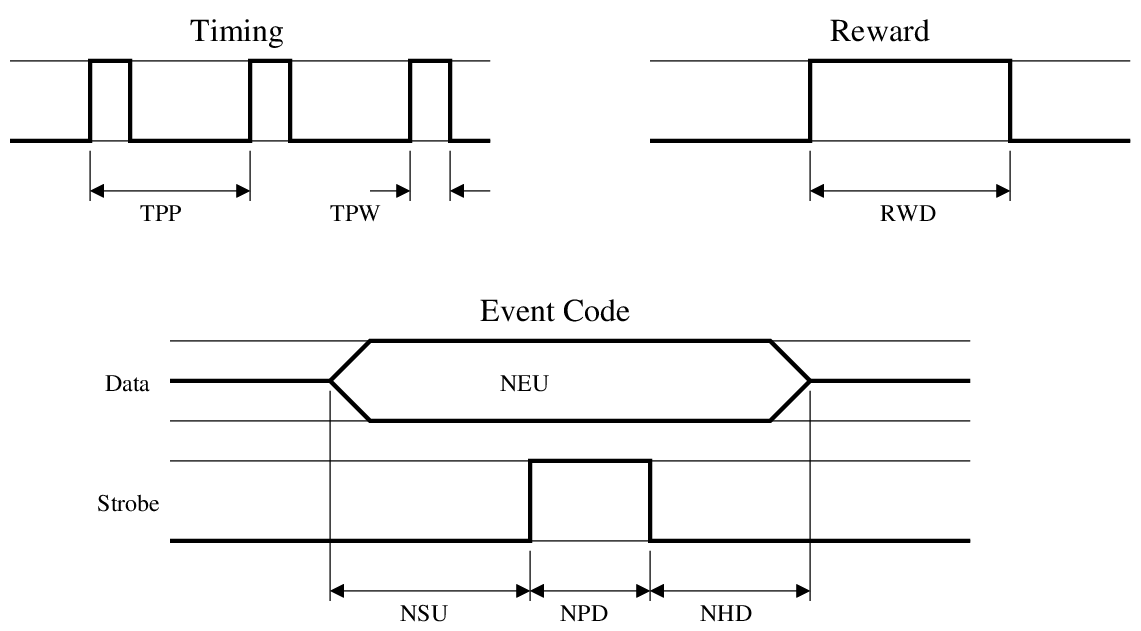
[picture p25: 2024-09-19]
manuals-src/figs/timing.png

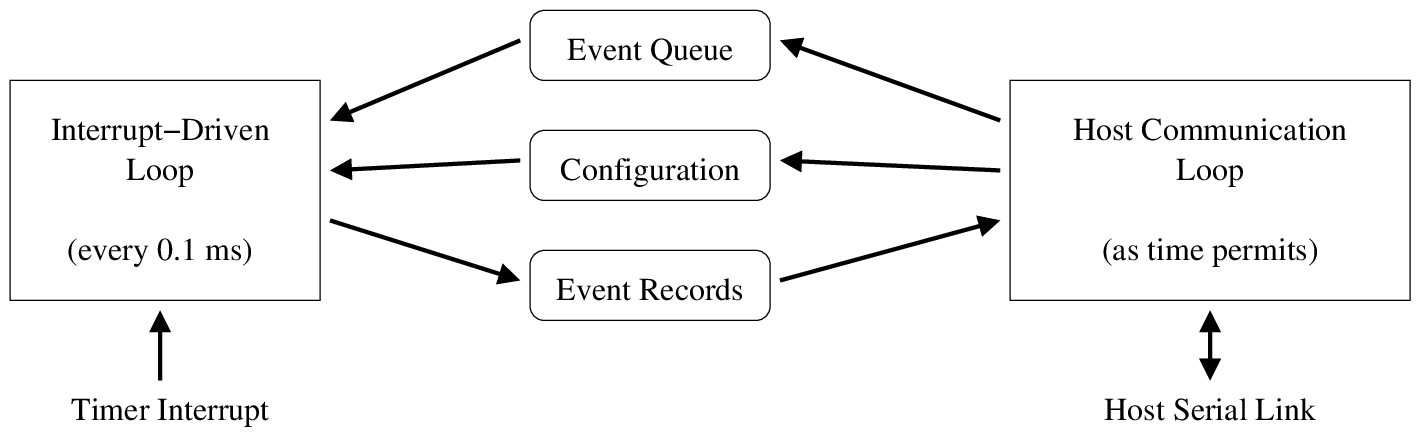
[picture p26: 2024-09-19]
manuals-src/figs/firmware.png

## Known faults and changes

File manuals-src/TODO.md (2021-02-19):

# Attention Circuits Control Laboratory - I/O SynchBox project - Manual
# Change log and to-do list.
Written by Christopher Thomas.

## To-do list:

* Update command list and description (last update was 2018).
* For each folder in "hardware-main" and "hardware-periphs", add a document
section with discussion, photos, schematics, board-layouts, BOMs, etc.
* Make a table of boards and peripherals in the main document section
(info in the top-level README file).
* Discuss pre-amp/filter circuit (abbreviated version of aux-filterdoc).

## Abbreviated changelog (most recent changes first):

* 19 Feb 2021 --
Initial repository upload.

_This is the end of the file._

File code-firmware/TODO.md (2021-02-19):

# Attention Circuits Control Laboratory - I/O SynchBox project
# Change log, bug list, and feature request list.
Written by Christopher Thomas.

## Bugs and feature requests:

* Debug monitor flagging analog changes doesn't work. Not sure why.

* Debug monitor of analog has unused "dead time" code.

* Need to add better GPIO support in general.

* Allow joystick filtering to be configured separately from light sensors.

* Have Makefile targets for 115kbaud and 500kbaud hex files.

* Allow commands to be queued for release when light sensor state changes.

* Ben had measured long-term timestamp drift between Unity and Arduino of
about 600ppm. This seemed to be due to stepwise glitches. See 18-19 sept
2018 email chain.

## Abbreviated changelog (most recent changes first):

* 11 Mar 2020 --
Fixed subtle timing and atomic-lock issues with timing pulses, reward
pulses, and event codes.

* 28 Jan 2020 --
Added second reward and second timing channel. Made "strobe" optional for
event codes (full 16 bits without).

* 03 Oct 2018 --
Fixed potential locking bug with `StartAnalogRead_ISR()` with nested
interrupts.

* 03 Oct 2018 --
Rewrote digital filtering code to carry residue forward, fixing the
terrible slope quantization problem. Made filter bits per-instance.

_This is the end of the file._

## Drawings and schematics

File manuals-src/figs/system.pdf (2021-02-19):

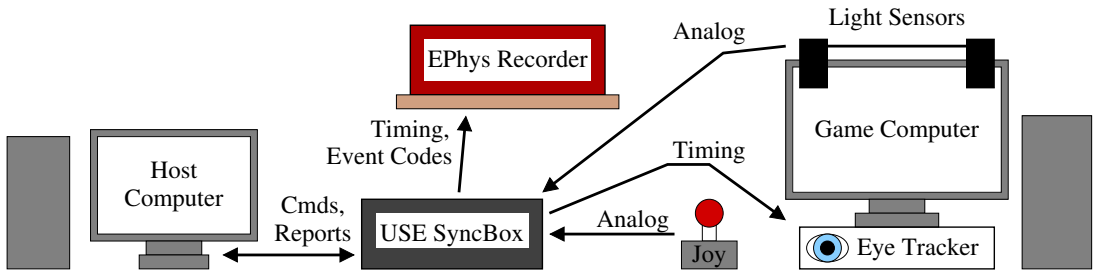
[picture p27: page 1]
Game Computer; Eye Tracker; Host Computer; EPhys Recorder; USE SyncBox; Light Sensors; Timing,; Timing; Joy; Event Codes; Analog; Reports; Cmds,

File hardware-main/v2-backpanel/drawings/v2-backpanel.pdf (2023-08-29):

# Back Faceplate

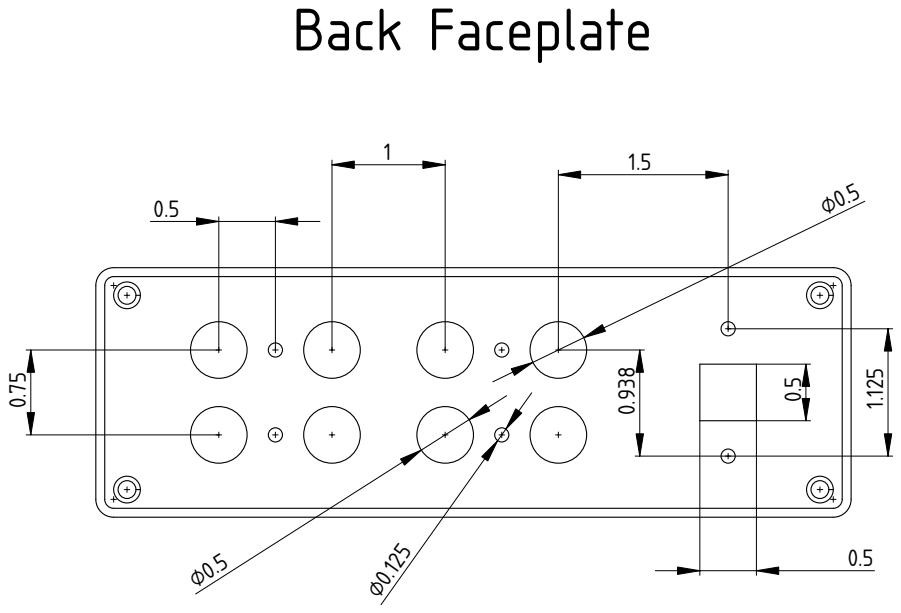
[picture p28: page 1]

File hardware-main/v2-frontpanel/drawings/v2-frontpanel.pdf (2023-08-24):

# Fro

# nt F

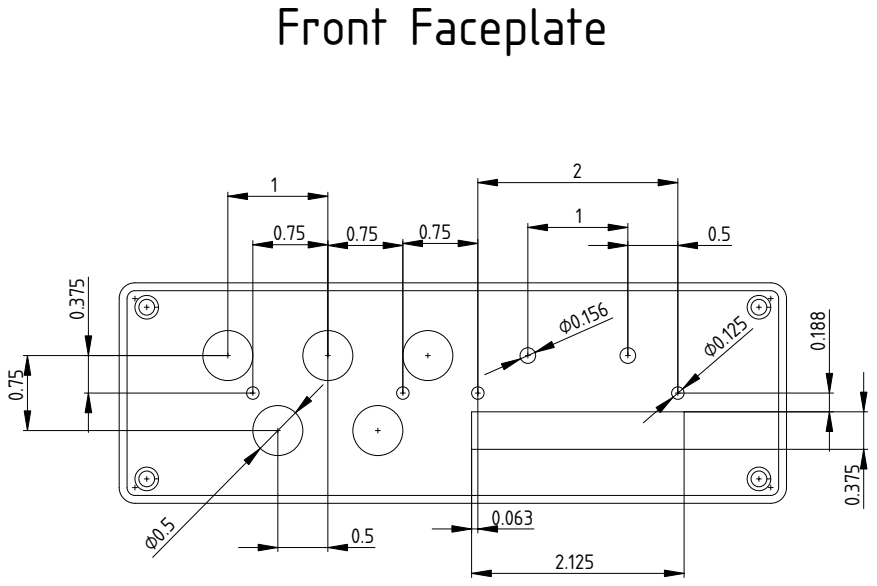
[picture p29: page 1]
ace; plate

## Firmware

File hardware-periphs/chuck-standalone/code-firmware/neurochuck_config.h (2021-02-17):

// Attention Circuits Control laboratory - Nunchuck adapter
// Configuration values and switches
// Written by Christopher Thomas.
// Copyright (c) 2021 by Vanderbilt University. This work is released under
// the Creative Commons Attribution-ShareAlike 4.0 International License.


//
// Diagnostics constants

#define VERSION_STR "20170810"

#define DEVICETYPE "Neurochuck"
#define DEVICESUBTYPE "v1"

// This toggles availability of debugging commands.
#define DEBUG_AVAILABLE 0


//
// Pin configuration constants

// Configuration switches for board type.
#define BOARD_PRO_TRINKET 1
#define BOARD_PRO_TRINKET_5V 1

#define BOARD_NANO 0

// Run power from I/O lines, per Ben and Marcus's sample unit.
#define BOARD_TRINKET_POWER_KLUDGE 1

// Use the built-in Arduino status LED.
#define LED_USE_BUILTIN 1


//
// Nunchuck configuration constants

// Scrambled (Wii) vs unscrambled (Wii + clones) mode.
#define USE_SCRAMBLED_MODE 0


// Digital I/O lines.
// These use AVR numberings.

// NOTE - The explicit cast is important, so that we don't waste a lot
// of time taking the complement when masking out a bit.

#if BOARD_PRO_TRINKET

// Fake power rails for the nunchuck adapter.
// On the Pro Trinket, these are C2/C3 (Ain 2/3).
#define PIN_FAKEPOWER_PORT PORTC
#define PIN_FAKEPOWER_DIRECT DDRC
#define PIN_FAKEPOWER_LOW_BIT ( (uint8_t) (1 << 2) )
#define PIN_FAKEPOWER_HIGH_BIT ( (uint8_t) (1 << 3) )

// Pull-down strap for auto-startup.
// On the Pro Trinket, this is B0 (Dio8).
#define PIN_AUTOSTART_PORT PORTB
#define PIN_AUTOSTART_INPUT PINB
#define PIN_AUTOSTART_DIRECT DDRB
#define PIN_AUTOSTART_BIT ( (uint8_t) (1 << 0) )

// Status LED pin.
// On the Pro Trinket, this is either the built-in (B5/SCK/Dio13) or B1 (Dio9).
#define PIN_LED_PORT PORTB
#define PIN_LED_DIRECT DDRB
#if LED_USE_BUILTIN
#define PIN_LED_BIT ( (uint8_t) (1 << 5) )
#else
#define PIN_LED_BIT ( (uint8_t) (1 << 1) )
#endif

// BOARD_PRO_TRINKET
#endif

#if BOARD_NANO

// FIXME - Nano NYI.

// BOARD_NANO
#endif


//
// Host link constants

// Host link baud rate.
// 115.2 and 500.0 have decent hardware support.
#define HOST_BAUD 115200
//define HOST_BAUD 500000

// Default settings vary depending on whether we're in automatic or manual
// mode.

// Manual mode.

#define DEFAULT_MANUAL_ECHO 1
#define DEFAULT_MANUAL_TSTAMP 1
#define DEFAULT_MANUAL_LOG_INTERVAL 1000 /* 10 Hz */
#define DEFAULT_MANUAL_BLINK 1
#define DEFAULT_MANUAL_POLL_INTERVAL 100 /* 100 Hz */

// Autostart mode.

#define DEFAULT_AUTO_ECHO 0
#define DEFAULT_AUTO_TSTAMP 0
#define DEFAULT_AUTO_LOG_INTERVAL 0 /* As fast as possible. */
#define DEFAULT_AUTO_BLINK 1
#define DEFAULT_AUTO_POLL_INTERVAL 0 /* As fast as possible. */

// NOTE - We're not using verbosity settings. Output is always terse.


//
// Timing constants


// Stuff that doesn't vary from board to board.

// RTC ticks per second.
// Match the Neurarduino's convention.
#define RTC_TICKS_PER_SECOND 10000ul

// RTC ticks per LED-control tick.
// Sampling rate is 16 Hz.
#define RTC_TICKS_PER_LED_TICK 625


// Board-specific stuff.

#if BOARD_PRO_TRINKET

// The clock speed depends on the voltage.
#if BOARD_PRO_TRINKET_5V
#define CPU_SPEED 16000000ul
#else
#define CPU_SPEED 12000000ul
#endif

// BOARD_PRO_TRINKET
#endif

#if BOARD_NANO

// FIXME - Nano NYI.

// BOARD_NANO
#endif


//
// This is the end of the file.

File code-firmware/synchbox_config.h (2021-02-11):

// Attention Circuits Control laboratory - I/O SynchBox project
// Configuration values and switches
// Written by Christopher Thomas.
// Copyright (c) 2021 by Vanderbilt University. This work is released under
// the Creative Commons Attribution-ShareAlike 4.0 International License.


//
// Diagnostics constants

#define VERSION_STR "20210211"

#define DEVICETYPE "I/O SynchBox"
#define DEVICESUBTYPE "v1"

// This toggles availability of debugging commands.
#define DEBUG_AVAILABLE 1
// Debug trigger dead time (to avoid noise-induced re-triggering).
// This is in ticks.
#define DEBUG_DEADTIME 10
// Length of the debugging reward pulse. This is in ticks.
#define DEBUG_REWARDLENGTH 1000


//
// Pin configuration constants

// Digital outputs.

// Reward is on Arduino D11, which is AVR B5.
// Second reward is on Arduino D10, which is AVR B4.
// Timing is on Arduino D12, which is AVR B6.
// Second timing is on Arduino D13, which is AVR B7.
// LED is on Arduino D4, which is AVR G5.
// Formerly on Arduino D8, which is AVR H5.
// NOTE - This is ATMega2560-specific!

// NOTE - The explicit cast is important, so that we don't waste a lot
// of time taking the complement when masking out a bit.

#define REWARD_PORT PORTB
#define REWARD_DIRECTION DDRB
#define REWARD_BIT ( (uint8_t) (1 << 5) )
#define REWARD_DESC "D11/B5/GP05"

#define REWARD2_PORT PORTB
#define REWARD2_DIRECTION DDRB
#define REWARD2_BIT ( (uint8_t) (1 << 4) )
#define REWARD2_DESC "D10/B4/GP04"

#define TIMING_PORT PORTB
#define TIMING_DIRECTION DDRB
#define TIMING_BIT ( (uint8_t) (1 << 6) )
#define TIMING_DESC "D12/B6/GP06"

#define TIMING2_PORT PORTB
#define TIMING2_DIRECTION DDRB
#define TIMING2_BIT ( (uint8_t) (1 << 7) )
#define TIMING2_DESC "D13/B7/GP07"

#define LED_PORT PORTG
#define LED_DIRECTION DDRG
#define LED_BIT ( (uint8_t) (1 << 5) )

// Additional digital I/Os for debugging.
// These are in the v2 case's GPIO block.
// Debug trigger is on Arduino D6, AVR H3, GPIO 0.
// Debug monitor is on Arduino D7, AVR H4, GPIO 1.

#define DEBUGTRIG_PORT PORTH
#define DEBUGTRIG_INPUT PINH
#define DEBUGTRIG_DIRECTION DDRH
#define DEBUGTRIG_BIT ( (uint8_t) (1 << 3) )
#define DEBUGTRIG_DESC "D6/H3/GP00"

#define DEBUGMON_PORT PORTH
#define DEBUGMON_DIRECTION DDRH
#define DEBUGMON_BIT ( (uint8_t) (1 << 4) )
#define DEBUGMON_DESC "D7/H4/GP01"

// Event code handshaking header.
// These are Atmel I/O register IDs.
// NOTE - This is ATMega2560-specific!
// C0..C7 is pin 37..30, L0..L7 is pin 49..42.
// Setting things up so that Data15..Data0 is pins 30..37,42..49.
// To strobe, just flicker the MSB.
#define EVCODE_PORT_H PORTC
#define EVCODE_PORT_L PORTL
#define EVCODE_DDR_H DDRC
#define EVCODE_DDR_L DDRL

// Analog inputs.
// These are Arudino analog pin IDs.
// NOTE - The Arduino's analog IDs match the ATmega2560's ADC input IDs.
// This is ATmega2560-specific!
#define JOY_X_PIN 0
#define JOY_Y_PIN 1
#define JOY_C_PIN 2
#define OPT_L_PIN 4
#define OPT_R_PIN 5

// Analog precision: 8 or 16 bits.
// The full scale range corresponds to 0V..2.56V in both cases.
#define ANALOG_16BIT 0

// Noise suppression filter.
// This has an exponential smoothing filter for LPF, and outlier rejection for
// spike suppression.
// The exponential smoothing filter gives new samples 1 part in 2^n weight.
// The outlier rejection filter rejects samples whose squared distance is 2^m
// times the variance. It uses its own LPF for both its averege and variance.
// Setting either LPF tuning parameter to 0 disables that filter.
// There are 5 analog channels, with round-robin sampling every 2 ticks. This
// means the native sampling rate per channel is 1 kHz.
#define AN_FILTER_LPF_BITS_DEFAULT 2
#define AN_FILTER_SPIKE_LPF_BITS_DEFAULT 6
#define AN_FILTER_SPIKE_SIZE_BITS_DEFAULT 2


//
// Host link constants

// Host link baud rate.
// 115.2 can be done with high precision. 230.4 with coarser precision.
// 500.0 can be done with high precision and is supported. 250 isn't.
// FIXME - 230 is unreliable with stock hardware. Ditto with an FTDI dongle.
#define HOST_BAUD 115200
//define HOST_BAUD 230400
//define HOST_BAUD 500000

// Echo.
#define ECHO_DEFAULT 1

// Default verbosity and reporting interval (in ticks).
#define DEFAULT_VERBOSITY VERB_FULL
// FIXME - Set a safe logging rate and let the user modify it.
// The eye-tracker runs at 300 Hz. NOTE - The closest we can get is 303.
// Verbose output at 115.2 tops out around 150 Hz.
#define DEFAULT_LOGINTERVAL 100 /* 100 Hz */
//define DEFAULT_LOGINTERVAL 33 /* 303.03... Hz */


//
// Timing constants

// CPU speed is the same for any of the AVR Arduino boards that we'd use.
// Make it a macro instead of an inline constant in case we need to swap out crystals for UART reasons.
#define CPU_SPEED 16000000ul

// Number of RTC ticks per second.
// We want better precision than milliseconds, but only want a 32-bit timestamp; so, custom ticks.
#define RTC_TICKS_PER_SECOND 10000ul
// FIXME - Debugging value that won't alias much with the standard value.
//define RTC_TICKS_PER_SECOND 6899ul

// Nested interrupt toggle.
// We don't need this at 115.2 kbaud, but do need it at 500 kbaud, so that
// we can service multiple UART interrupts per tick.
#define ALLOW_NESTED_INTERRUPTS 1



//
// This is the end of the file.

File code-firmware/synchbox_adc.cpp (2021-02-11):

// Attention Circuits Control laboratory - I/O SynchBox project
// ADC routines - Mega 2650
// Written by Christopher Thomas.
// Copyright (c) 2021 by Vanderbilt University. This work is released under
// the Creative Commons Attribution-ShareAlike 4.0 International License.


//
// Includes

#include "synchbox_includes.h"



//
// Global variables

// ADC sample.
// This is volatile, because ISRs can update it.
volatile bool adc_data_valid;
volatile analog_sample_t adc_data;



//
// Constants

// Reference portion of ADMUX.
// We're using the internal 2.56V reference.
// Results are left-adjusted, because we only need the MS 8 bits.
// We need a capacitor on the AREF pin; the Mega 2560 board has one.
#define ADMUX_BASE 0xe0

// Analog output pin LUT for ADMUX.
// NOTE - Input pins 8..15 require setting MUX5, which is in ADCSRB.
// Make life easier and limit ourselves to 0..7, so that MUX5 is always 0.
#define ADMUX_PIN_COUNT 8
const uint8_t admux_lsb_lut[ADMUX_PIN_COUNT] =
{
  // Conveniently, code = input number for single-ended inputs 0..7.
  0x00, 0x01, 0x02, 0x03,
  0x04, 0x05, 0x06, 0x07
};

// We want the comparator off, MUX5 to 0, and trigger to free running (0).
// Trigger mode is actually ignored, as we're disabling auto-triggering.
#define ADCSRB_VALUE 0x00

// We want three states: ADC off, ADC ready, and ADC start conversion.
// Remember that we need to write 1 to ADIF to clear it, not 0.
// That said, we can ignore ADIF and just watch ADSC.
// We want a clock divisor of /128, for an ADC clock of 125 kHz (9.6 ksps).
#define ADCSRA_OFF 0x17
#define ADCSRA_READY (ADCSRA_OFF | 0x80)
#define ADCSRA_STARTMASK 0x40
#define ADCSRA_START (ADCSRA_READY | ADCSRA_STARTMASK)



//
// Functions


// Initializes the analog to digital converter.

void InitADC()
{
  ATOMIC_BLOCK(ATOMIC_RESTORESTATE)
  {
    adc_data_valid = false;
    adc_data = 0;

    // FIXME - All of this is m2560-specific.

    // Disable digital inputs.
    DIDR0 = 0x00;
    DIDR2 = 0x00;
    // DIDR1 is for the comparator, not the ADC.

    // Make sure the ADC is off.
    ADCSRA = ADCSRA_OFF;

    // Set the remaining control registers to reasonable values.
    ADCSRB = ADCSRB_VALUE;
    ADMUX = ADMUX_BASE | admux_lsb_lut[0];

    // Turn the ADC on.
    // NOTE - This may take a little while to stabilize!
    // Don't trust the first few conversion values.
    // The first conversion will also take about twice as long.
    ADCSRA = ADCSRA_READY;
  }
}


// Performs ADC housekeeping.
// This should be called from within an ISR, or else wrapped in a lock.
// This will notice when an ADC conversion completes and copy the
// data to a safe location, resetting the ADC.
// Returns true if the ADC is available (idle) and false if it's busy.

bool PollADC_ISR()
{
  uint8_t adcsra_value;
  uint16_t adcval_high;
  uint16_t adcval_low;

  // No lock needed, as we're being called from an ISR.

  // NOTE - Only check this if we haven't _already_ checked it!
  if (!adc_data_valid)
  {
    // See if a conversion has completed.
    adcsra_value = ADCSRA;
    if (0 == (adcsra_value & ADCSRA_STARTMASK))
    {
#if ANALOG_16BIT
      // Record the full 16 bits.
      // This is still left-adjusted, so 0xffff is 2.56V.
      // Read LS, then MS; MS resets.
      adcval_low = ADCL;
      adcval_high = ADCH;
      adc_data = (adcval_high << 8) | (adcval_low);
#else
      // Record the MS byte of this sample.
      // It's left-adjusted, so this gives us the top 8 bits.
      adc_data = ADCH;
#endif

      // We now have valid data.
      adc_data_valid = true;
    }
  }

  return adc_data_valid;
}


// Sets up an ADC conversion using the specified input.
// This should be called from within an ISR, or else wrapped in a lock.
// NOTE - This should only be called when PollADC_ISR() indicates the ADC is free!

void StartAnalogRead_ISR(int pin_id)
{
  uint8_t admux_value;

  if ((0 <= pin_id) && (ADMUX_PIN_COUNT > pin_id))
  {
    // Select our input.
    admux_value = admux_lsb_lut[pin_id];
    admux_value |= ADMUX_BASE;
    ADMUX = admux_value;

    // Clear data flags and record.
    adc_data_valid = false;
    adc_data = 0;

    // Trigger the ADC.
    ADCSRA = ADCSRA_START;
  }
}



//
// Class Implementations


// Constructor.
// Initialize to stable defaults. Set default bit values here too.
// Flag as needing further initialization.

NoiseFilter::NoiseFilter(void)
{
  need_init = true;
  averagefuzz = 0;
  averagevar = 0;
  variance = 0;
  last_valid = 0xaa; //FIXME - Debug value.
  fuzz_lpf_bits = AN_FILTER_LPF_BITS_DEFAULT;
  var_lpf_bits = AN_FILTER_SPIKE_LPF_BITS_DEFAULT;
  spike_shift_bits = AN_FILTER_SPIKE_SIZE_BITS_DEFAULT;
}


// Reconfigure filter parameters.
// NOTE - This should be done within an atomic block!

void NoiseFilter::SetFilterTimes(uint8_t new_fuzz, uint8_t new_var,
  uint8_t new_spike)
{
  // Copy the new state information over and flag as needing reinitialization.
  fuzz_lpf_bits = new_fuzz;
  var_lpf_bits = new_var;
  spike_shift_bits = new_spike;
  need_init = true;
}


// Processes a sample, returning the filtered value.
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

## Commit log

2021-02-17 Started adding PCB files. Set up structure for mechanical files.
    [adapter-brainamp.bottom.gbr, adapter-brainamp.bottommask.gbr, adapter-brainamp.fab.gbr, adapter-brainamp.outline.gbr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]
2021-02-17 Folded in ribbon cable splitter and Intan adapter, from the Neuro2k dev tree.
    [evbig-shell.fcstd, pcb-evbig.bottom.gbr, pcb-evbig.bottommask.gbr, pcb-evbig.fab.gbr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]
2021-02-17 Finished moving hardware content and vendor docs into the tree.
    [clamp-body-inches.stl, clamp-locator-cap-inches.stl, clamp-locator-cap-mm.stl, clamp-wire-cap-inches.stl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]
2021-02-17 Added nunchuck stand-alone device.
2021-02-18 Added 'pcb2png' utility script. Added Makefiles to build release packages for hardware-main, and a stub for hardware-periphs.
2022-10-03 Summarized flow control issue with clone boards, since I ran into it again.
2022-12-06 Added hardware squid. Turned symlink documentation figures into manual copies.
    [evcode-squid-bottom-shell.stl, evcode-squid-top-shell.stl, event-squid-8bit.fcstd]
2023-02-27 Added targets for burning and talking to clone boards that use USB0 and don't have flow control.
2023-08-23 Added my blank faceplate model. Overhauled front panel faceplate freecad design. Exported front plate mesh.
    [faceplate-hm904-blank.iges, v2-faceplates.fcstd, v2-front-panel.stl, v2-frontpanel.fcstd]
2023-08-23 Added IGES model of front panel.
    [v2-frontpanel.iges]
2023-08-24 Added front panel mesh and model to release package.
    [synchbox-frontpanel-mesh.stl, synchbox-frontpanel-model.iges, v2-frontpanel.stl]
2023-08-24 Overhauled back panel CAD.
    [synchbox-backpanel-mesh.stl, synchbox-backpanel-model.iges, v2-backpanel.fcstd, v2-backpanel.iges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]
2023-08-24 Added decent back panel drawing.
    [v2-backpanel.fcstd]
2023-08-24 Added decent front panel drawing.
    [v2-frontpanel.fcstd]
2023-08-24 Clarified stand-off type for assembly BOM.
2023-08-29 Fixed design errors in back panel faceplate.
    [v2-backpanel.fcstd, v2-backpanel.stl]
2023-09-21 Added BNC connector soldering notes.
2023-09-22 Fixed back panel countersink. Trimmed front and back panel lip for 3d printing.
    [synchbox-backpanel-mesh.stl, synchbox-backpanel-model.iges, synchbox-frontpanel-mesh.stl, synchbox-frontpanel-model.iges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]
2024-07-31 Added simplified faceplate with looser tolerances for easier filament printing.
    [faceplate-hm904-blank-printable.iges]
2025-08-16 Added simplified front and back panel meshes that are printable without supports.
    [synchbox-backpanel-simple-mesh.stl, synchbox-backpanel-simple-model.iges, synchbox-frontpanel-simple-mesh.stl, synchbox-frontpanel-simple-model.iges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]
